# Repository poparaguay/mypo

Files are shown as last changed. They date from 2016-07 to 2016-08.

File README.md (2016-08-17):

# MyPO Board

Myo Armband + PO Paraguay
========
A board that connects the different parts of the system, demonimated MyPo. It is the interface between the Myo Armband sensor and the advanced prosthetic. It is composed of an Arduino board and a Bluetooth 4.0 module, with a custom firmware. Next are the different parts that compose this board.

Components
----

* MyPo Board
    ```
    
    Designed by Po Paraguay and manufactured by https://oshpark.com/ by uploading the mypo.brd file to the webpage
    
    Allows to flash the bluetooth module from the board itself
    
    ```
* Bluetooth BLE HM-11 CC2541 SoC 
    ```
    
    Flash the board by following these steps: https://github.com/RedBearLab/CCLoader
    
    Flash this file  "MyoBridge_CC2541.hex" to the CC2541 chip
     
    ```
* Arduino Pro Mini 328 5V/16Mhz.
* MicroServo 

    ```
    
    3 x TowerPro MG92B.  (Torque (4.8v): 3.1kg/cm - (6.0v): 3.5kg/cm)
    
    ```
    
* Battery: Li-Ion 1S 2500mAh 18650 
* Charge/Discharge module with voltage protection:

    ```
    http://goo.gl/Kd2iIu 
    
    ```
* 3.3V Regulator
    ```
AMS11171A LOW DROPOUT VOLTAGE REGULATOR 
http://www.advanced-monolithic.com/pdf/ds1117.pdf
    ```

*Passive components SMD  (0805: 0.08" × 0.05" (2,0 mm × 1,25 mm)  1/8 W)
    ```
- Resistors 1R/2R, where 1R is the value of any resistor and 2R is the double of that
-  100nF Capacitor
    ```

Characteristics
----

* Does not need an external computer to run
* The actual processing of the data is done by the Myo armband
* Uses the MyoBridge library:
    ```
    https://github.com/vroland/MyoBridge 
    ```
* Independent control of up to 3 servos: 
    ```
    SERVO1 : Port 5
    
    SERVO2 : Port 6
    
    GPIO1  : Port 9
    
    ```
* Virtual communication (Bluetooth - Arduino)
    ```
    
    RX Arduino to TX Bluetooth : Port 2
    
    TX Arduino to RX Bluetooth : Port 3
   
    ```

Author
----------
* Mateo Acosta - macosta@po.com.py

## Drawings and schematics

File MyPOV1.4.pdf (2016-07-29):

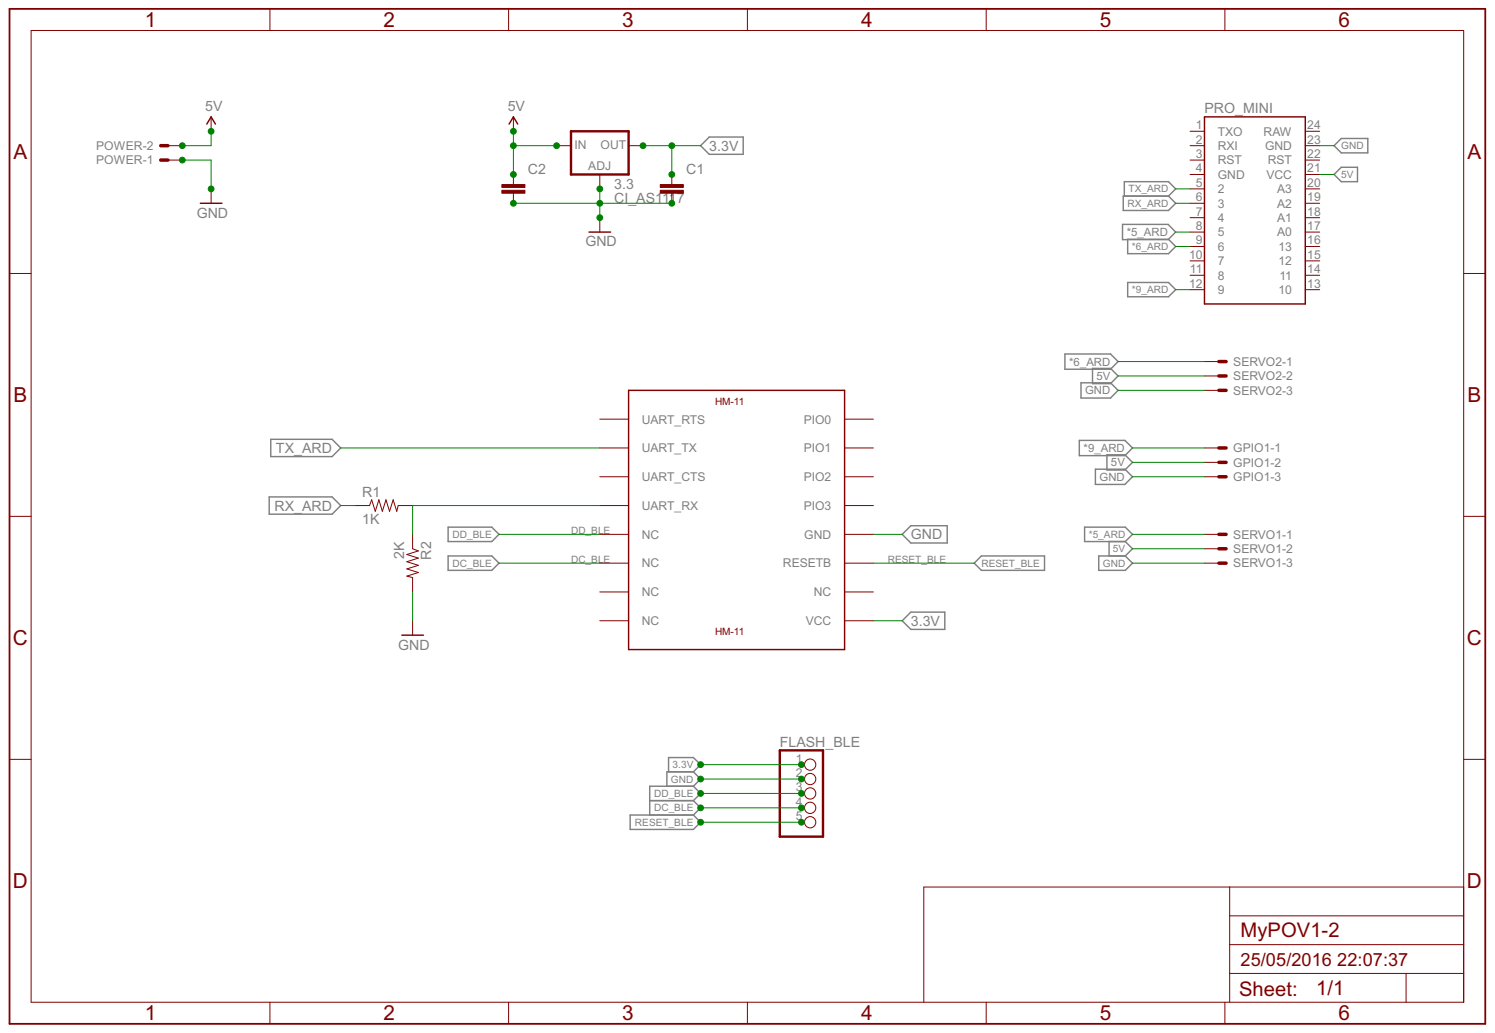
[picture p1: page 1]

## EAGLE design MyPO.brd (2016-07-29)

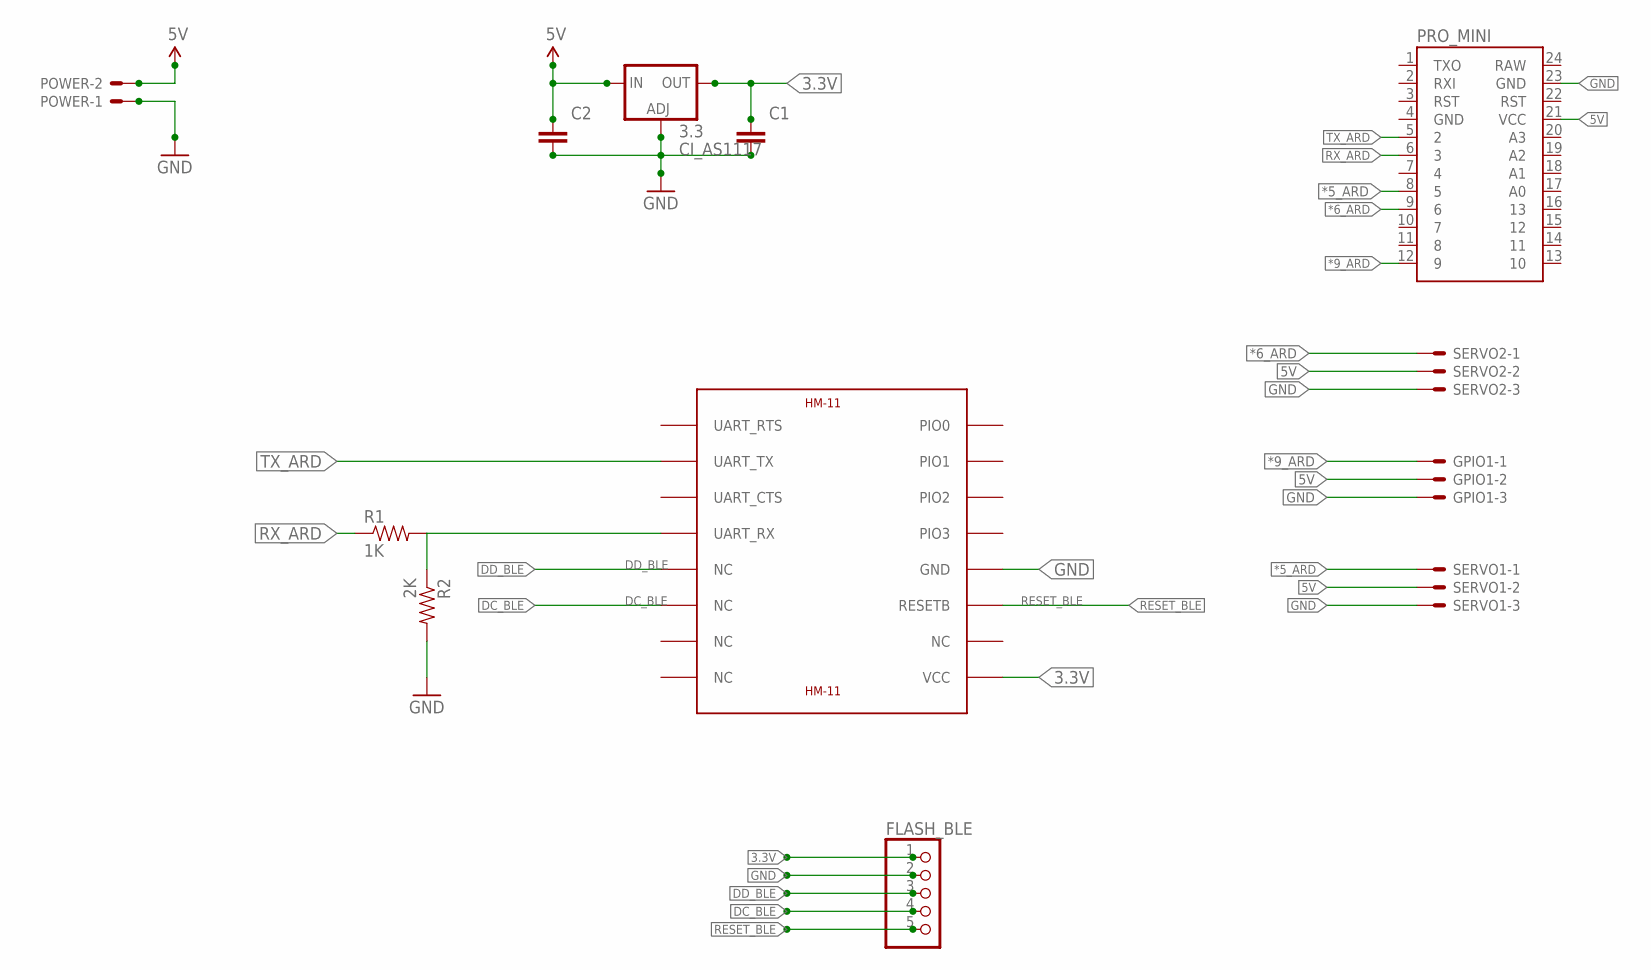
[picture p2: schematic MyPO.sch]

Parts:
3.3: CI_AS1117; DPACK
BLE: HM-11
C1, C2: CAPACITOR-0805; C0805
FLASH_BLE: PINHD-1X55X2MM; 1_05X2MM
GPIO1: JST-XH-03-PIN-LONG-PAD; JST-XH-03-PACKAGE-LONG-PAD
POWER: JST-XH-02-PIN-LONG-PAD; JST-XH-02-PACKAGE-LONG-PAD
PRO_MINI: ARDUINO_MINI
R1: 1K; R0805
R2: 2K; R0805
SERVO1, SERVO2: JST-XH-03-PIN-LONG-PAD; JST-XH-03-PACKAGE-LONG-PAD

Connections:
3.3V: 3.3.4 (OUT), BLE.VCC, C1.1, FLASH_BLE.1
5V: 3.3.3 (IN), C2.1, GPIO1.2, POWER.2, PRO_MINI.21 (VCC), SERVO1.2, SERVO2.2
*5_ARD: PRO_MINI.8 (5), SERVO1.1
*6_ARD: PRO_MINI.9 (6), SERVO2.1
*9_ARD: GPIO1.1, PRO_MINI.12 (9)
DC_BLE: BLE.NC@6 (NC), FLASH_BLE.4
DD_BLE: BLE.NC@5 (NC), FLASH_BLE.3
GND: 3.3.1 (ADJ), BLE.GND, C1.2, C2.2, FLASH_BLE.2, GPIO1.3, POWER.1, PRO_MINI.23 (GND), R2.2, SERVO1.3, SERVO2.3
unnamed: BLE.UART_RX, R1.2, R2.1
RESET_BLE: BLE.RESETB, FLASH_BLE.5
RX_ARD: PRO_MINI.6 (3), R1.1
TX_ARD: BLE.UART_TX, PRO_MINI.5 (2)

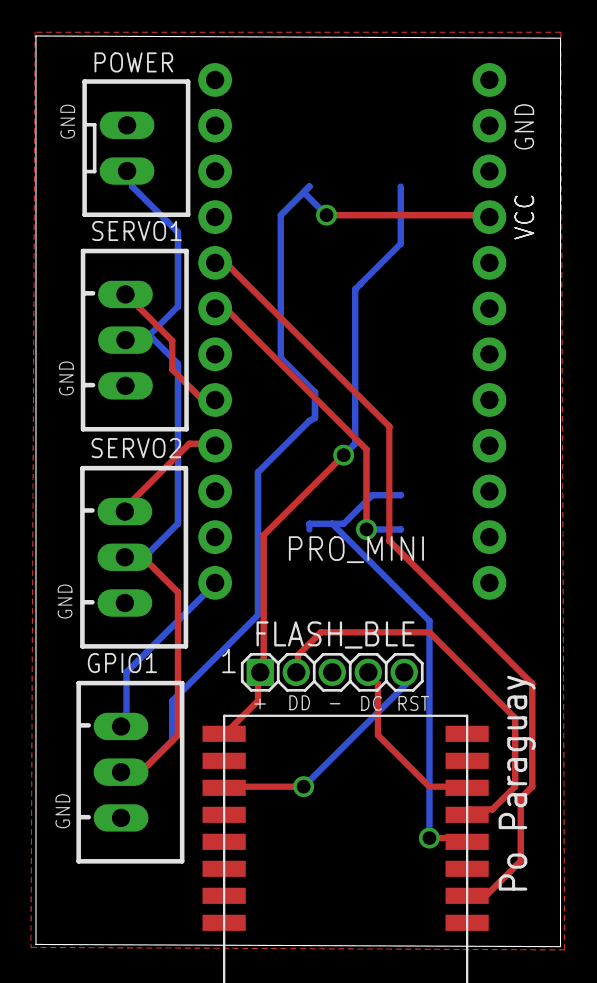
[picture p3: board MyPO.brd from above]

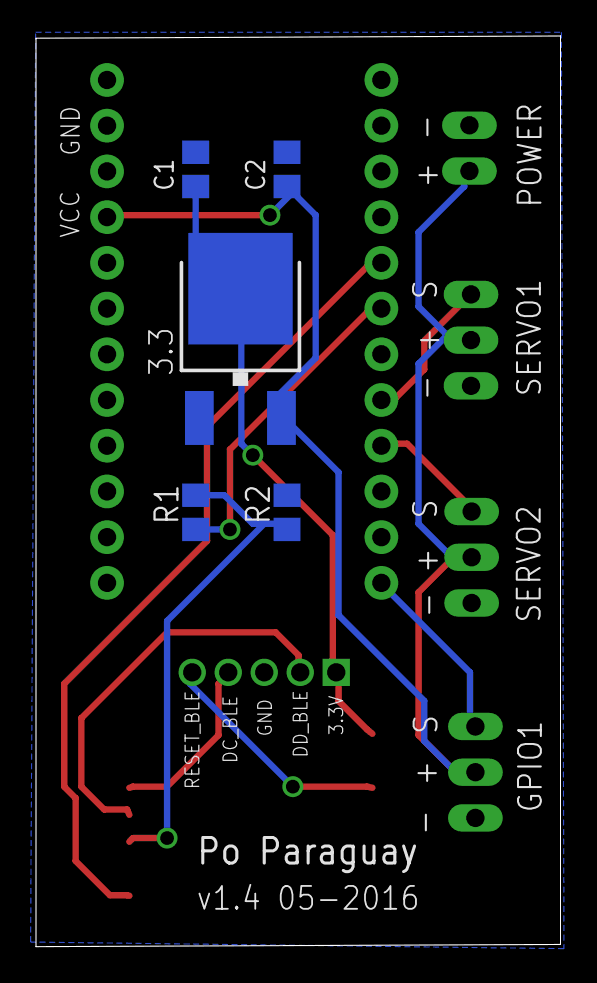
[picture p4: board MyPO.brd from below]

Board: 2 copper layers, 29.1 x 50.6 mm, 12 parts (5 on the bottom side), 12 nets.

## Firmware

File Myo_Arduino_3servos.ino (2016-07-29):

#include <Servo.h>
#include <MyoBridge.h>
#include <SoftwareSerial.h>

//SoftwareSerial connection to MyoBridge
SoftwareSerial bridgeSerial(2,3);

//initialize MyoBridge object with software serial connection
MyoBridge bridge(bridgeSerial);

//declare a function to handle pose data
void handlePoseData(MyoPoseData& data) {

  //convert pose data to MyoPose
  MyoPose pose;
  pose = (MyoPose)data.pose;

  //print the pose
  Serial.println(bridge.poseToString(pose));

  move_hand(pose);

   //delay(100);
}

//a function to inform us about the current state and the progess of the connection to the Myo.
void printConnectionStatus(MyoConnectionStatus status) {
  
  //print the status constant as string
  Serial.println(bridge.connectionStatusToString(status));
}


Servo servo_thumb;  // objeto servo pulgar
Servo servo_index_middle;  // objeto servo indice y medio
Servo servo_ring_pinkie;  // objeto servo anular y meñique

void setup() {
  //initialize both serial connections
  Serial.begin(115200);
  bridgeSerial.begin(115200);

  //wait until MyoBridge has found Myo and is connected. Make sure Myo is not connected to anything else and not in standby!
  Serial.println("Searching for Myo...");
  for (int i=0; i<10;i++){digitalWrite(13, HIGH);delay(50);
  digitalWrite(13, LOW);delay(50);} 
 //initiate the connection with the status callback function
  bridge.begin(printConnectionStatus);
  digitalWrite(13, HIGH);
  delay(2000);
  digitalWrite(13, LOW);
  Serial.println("connected!");
  //declare a storage array for the hardware address
  byte address[6];
  //get the address and store it in our array
  bridge.getHardwareAddress(address);
  //print the hardware address in HEX format
  Serial.print("Hardware Address: 0x");
  for (int i=0;i<6;i++) {
    Serial.print(address[i], HEX);
  }
  Serial.println();
  
  //get the current battery level and print it
  byte batteryLevel = bridge.getBatteryLevel();
  Serial.print("Battery Level: ");
  Serial.println(batteryLevel);
  
  //short vibration to show we are ready
  bridge.vibrate(1);

  
  //set the function that handles pose events
  bridge.setPoseEventCallBack(handlePoseData);
  //tell the Myo we want Pose data
  bridge.enablePoseData();
  //make sure Myo is unlocked
  bridge.unlockMyo();

  //You have to perform the sync gesture to receive Pose data!

  servo_thumb.attach(9);  // attaches the servo on pin 3 to the servo object
  servo_index_middle.attach(6);  // attaches the servo on pin 5 to the servo object
  servo_ring_pinkie.attach(5);  // attaches the servo on pin 6 to the servo object
}

void loop()
{
  //update the connection to MyoBridge
  bridge.update();

  //MyoPose pose;
  //pose = (MyoPose)data.pose;
  //char a = bridge.poseToString(pose);

}

#define POS_THUMB_OPEN 150
#define POS_THUMB_CLOSE 40
#define POS_INDEX_MIDDLE_OPEN 150 // ya está
#define POS_INDEX_MIDDLE_CLOSE 40 // ya está
#define POS_RING_PINKIE_OPEN 170
#define POS_RING_PINKIE_CLOSE 30

int pos_thumb=0;
int pos_index_middle=0;
int pos_ring_pinkie=0;
int flag_openhand=0;

void move_hand(int pose)
{
  switch (pose) {
    case 0://MYO_POSE_REST
    //if (flag_openhand==1) {
    
     // }
      flag_openhand=0;
      LED_blink();
      break;
    case 1://MYO_POSE_FIST
      LED_blink();
      break;
    case 2://MYO_POSE_WAVE_IN
      pos_thumb = POS_THUMB_CLOSE;
      pos_index_middle = POS_INDEX_MIDDLE_CLOSE;
      pos_ring_pinkie = POS_RING_PINKIE_CLOSE;
      LED_blink();
      break;
    case 3://MYO_POSE_WAVE_OUT
      pos_thumb = POS_THUMB_OPEN;
      pos_index_middle = POS_INDEX_MIDDLE_OPEN;
      pos_ring_pinkie = POS_RING_PINKIE_OPEN;
      flag_openhand=1;
      LED_blink();
      break;
    case 4: //MYO_POSE_FINGERSPREAD
      LED_blink();
      break;
    case 5://MYO_POSE_DOUBLE_TAP
      LED_blink();
      break;
   }

 servo_thumb.write(pos_thumb);
 servo_index_middle.write(pos_index_middle);
 servo_ring_pinkie.write(pos_ring_pinkie);
}

void LED_blink ()
{
    digitalWrite(13, HIGH);delay(50);
    digitalWrite(13, LOW);delay(50);
}

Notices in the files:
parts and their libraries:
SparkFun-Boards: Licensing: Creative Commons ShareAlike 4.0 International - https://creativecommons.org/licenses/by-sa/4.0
